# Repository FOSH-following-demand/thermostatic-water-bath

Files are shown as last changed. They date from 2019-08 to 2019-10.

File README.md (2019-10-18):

# Open Source Thermostatic Water Bath 



### Welcome!


Thanks you for visiting this repository of this wonderful project!.

This document (The README file) is a hub to give you some guidance about all of what is happening here.

If you want to know more, please follow this quick links to jump to a specific section, or just scroll down to find out more!
  * [The problem involved](https://github.com/FOSH-following-demand/thermostatic-water-bath#the-problem)
  * [The solution we found](https://github.com/FOSH-following-demand/thermostatic-water-bath#the-solution)
  * [The idea behind the project](https://github.com/FOSH-following-demand/thermostatic-water-bath#the-idea)
  * [What we found interesting? ](https://github.com/FOSH-following-demand/thermostatic-water-bath#what-we-found)
  * [Find out more about](https://github.com/FOSH-following-demand/thermostatic-water-bath#get-involved)
  * [I don't understand something](https://github.com/FOSH-following-demand/thermostatic-water-bath#glossary)

## The problem:

In research and clinical laboratories, it is always useful to keep reagents or samples that are analyzed, at certain temperatures.
A _thermostatic bath_ is a device designed to maintain the temperature of the objects in contact with the fluid used.

In general, they are composed of electric heaters that heat distilled water (or other fluid) and, when they reach a certain temperature, they are automatically disconnected from the energy.

## The solution:

Our idea is to use efficiency and solidity as a basis, so we will use Peltier cells to take advantage of the Peltier effect, which is normally used as a thermoelectric cooler.

But, the advantage of using these cells, is that if we reverse the polarity, we could extract heat instead of generating it.

Therefore, we would have a thermostatic bath capable of generating heat or cold without modifying its design or changing any part.

The project will consist on the design and construction of the control circuit as well as the hardware involved, e. g. bath container, dissipation of heat, etc.

### The idea

The microcontrollers based on the [ATMEGA328p](https://store.arduino.cc/usa/arduino-uno-rev3) will be used mainly for the first tests and the calibration of the sensors.
```
Once this is done (by the way, you can check the code [here](https://github.com/FOSH-following-demand/thermostatic-wather-bath/tree/master/software/MCU)), the goal will be to use a __"We Mos D1 Mini"__ [board](https://wiki.wemos.cc/products:d1:d1_mini) as the main controller and, as a complement, the ability to connect to [Cayenne web services](https://mydevices.com/) as a monitor and remote control through IoT technology.
```
While this was a good idea, in the end, we are going to use a "_NODEMCU-32S_", The [NodeMCU ESP-32S](https://docs.zerynth.com/latest/official/board.zerynth.nodemcu_esp32/docs/index.html) is one of the development board created by NodeMcu to evaluate the ESP-WROOM-32 module. It is based on the ESP32 microcontroller that boasts Wifi, Bluetooth, Ethernet and Low Power support all in a single chip. Then, an internet connection will be built through the use of the [Mozilla WebThings Open Source IoT](https://iot.mozilla.org/) platform, which will be centralized in a hub ([Raspberry Pi 4](https://www.raspberrypi.org/products/raspberry-pi-4-model-b/)) for later operation and remote control.

The electric resistors if they do not have water are burned (if they do not have electronic protection circuits, as usual), with the design proposed in this project, we will try to avoid it by measuring the current that the cell consumes, so we can determine, without using another type of sensors, like a __DS18B20__ ([datasheet here](https://datasheets.maximintegrated.com/en/ds/DS18B20.pdf)), if the container where the piece is located, has enough distilled water or coolant (in case you want to cool below 0 deg C).

There is a lot of variety of Peltier cells, qualities and ways to get them. We have been guided by a Chinese manufacturer ([link here](https://peltiermodules.com/)) that briefly describes the characteristics of the product, but when we go to the tests, they perform as stated in the datasheet.

## What we found

In our studies, we used a Peltier Cell [TEC-12705](https://peltiermodules.com/peltier.datasheet/TEC1-12705.pdf) to start. After many thorough tests, we realized that it would not be able to heat quickly the water in the container (around 1 liter). Therefore, after a week of continuous tests, we change to a _new cell_, in this case, the [TEC-12715](https://peltiermodules.com/peltier.datasheet/TEC1-12715.pdf), which may seem only a little bigger than the 12705, but while the power of the 12705 is __50W__, the one of the 12715 is __150W__!

We had to get a more powerful 12v power supply, which are frequently used in DVR cameras, approximately 29 A of peak current, to improve the power.

We have managed to stabilize the temperature adequately in the range of +/- 0.1 °C, which made us very happy! Here are some [results](https://docs.google.com/spreadsheets/d/14x8ajXjDDJAvYHkvkYrGuCvhuu2BmfRY7JI32HTowtU/edit?usp=sharing).

[Here](https://docs.google.com/spreadsheets/d/1heXNcq8TzLmtxA4aUKqf4gO-YtcK64AZdO5G_QmcZ0U/edit?usp=sharing) is the most complete example on the peltier usage.

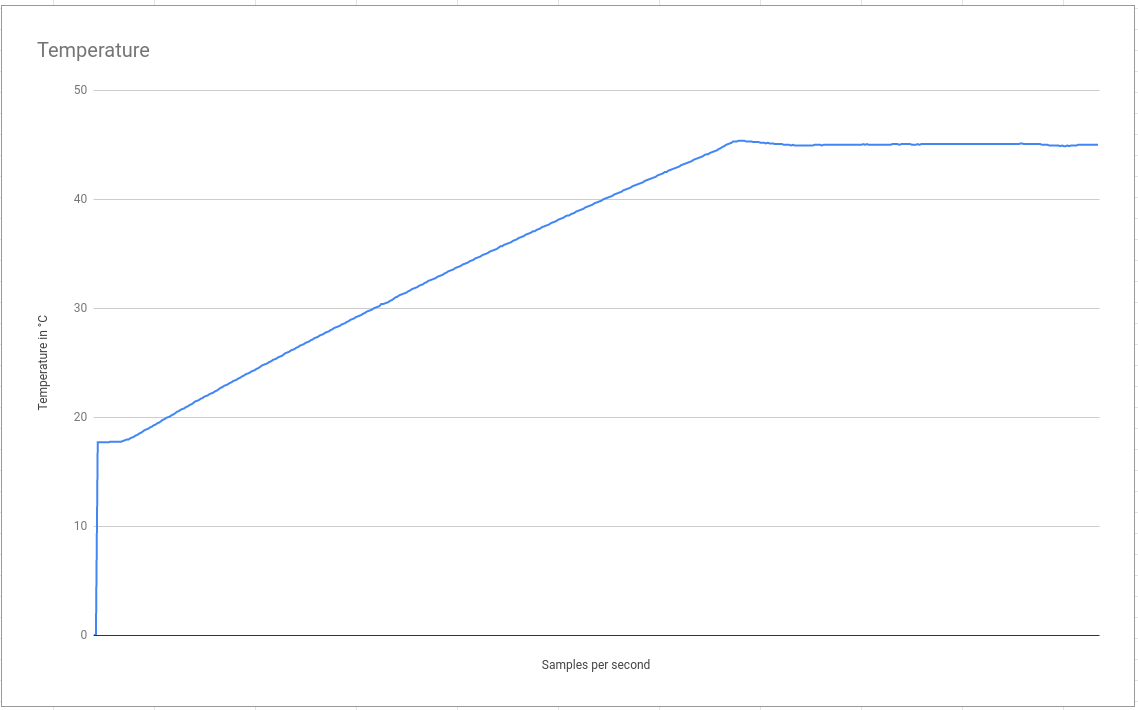
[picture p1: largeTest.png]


## Get involved

### Contribute
As we move forward, we will be contributing more and more things to the repository, if you like this project please contribute to it, after reading the [contributing](https://github.com/FOSH-following-demand/thermostatic-water-bath/blob/master/contributing.md) scheme.

### Development Plan

To follow the last changes made in the project, please follow this [link](https://github.com/FOSH-following-demand/thermostatic-water-bath/blob/master/dev_plan.md)

### Construction and Building

  To continue with the _Installation of Software_, please follow this [link](https://github.com/FOSH-following-demand/thermostatic-water-bath/tree/master/software/MCU)

  To continue with the _Building of Electronics_, please follow this [link](https://github.com/FOSH-following-demand/thermostatic-water-bath/tree/master/documentation/building)

  To continue with the _Building of the Hardware_, please follow this another [link](https://github.com/FOSH-following-demand/thermostatic-water-bath/blob/master/hardware/BOM/BOM.md)

  To continue with the _Building of the frame_, please click [here](https://github.com/FOSH-following-demand/thermostatic-water-bath/blob/master/hardware/frame/frame.md#3d-design-files-are-here)

### Thank you

by [TECSCI](https://github.com/tecsci)

### Glossary

  * __README File__: a document that introduces an open project to the public and any potential contributors
  * __repository__ or __repo__:a collection of documents related to your project, in which you create and save new code or content
  * __Issue__: the GitHub term for tasks, enhancements, and bugs for your projects

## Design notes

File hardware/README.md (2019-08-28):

# Hardware

This video made with a thermal camera shows us what the system is capable of.

Video

The settings that have been made for this video correspond to the software version 0.0.2

### Current features [version 0.0.2]:

If the sensor is not correctly connected at the beginning of the program, an alarm will be triggered that the only way to update it will be by restarting the microcontroller.

Video

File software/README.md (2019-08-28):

_Two libraries_ are currently being used, possibly 2 more would be missing, to improve the code.

One is called "__Peltier__" and the other is called "__lcdScreen__", both are designed to simplify the Arduino code and not make it so tedious to read and understand in order to modify it.

In effect, the libraries have given more work time since they needed a lot of testing and debugging,

With the PID control, most of the incidents have occurred, since although our setup was within the parameters taught in the code, their behavior was not very desirable and what was called an overshooting above the setpoint occurred, This led to a hunting and debouncing very frequently seen in these types of cells.

In addition to the challenge of using peltier cells for the thermostatic bath, we can say that the interest aroused by the use of them has generated more than one query in our group of nearby people.

Now we continue with the description of the libraries

# Available Commands on
- Peltier Library

```
createPeltier(uint8_t A,uint8_t B,uint8_t E, uint8_t pwm);

void coolFast();

void heatFast();

bool cool(bool activate, uint8_t pwmValue);

bool heat(bool activate, uint8_t pwmValue);

bool powerOff(bool confirm);

```
You have two options, one is to use a Driver as we will suggest later, although the other most frequently used is to use a Relay connected to one of the pins (In this case it would be the "Enable" pin you have defined), while that with the other system using a driver, you will not only be able to cool and heat without moving any electrical connection, but you will also have the possibility of using a PID control in your setup for temperature control.

- LCD Screen Library  (It is currently under development :fire: ...)
```
  initThis(char addr, int rows);

  bool turnOff();

  bool setActualTemp(float num);

  bool setCurrent(float amps);

  bool setEndTemp(float set);
```
This library facilitates the assembly of the user interface on the LCD screen (small GUI), it can be 16x02 or 20x4, both can be set in the library and thus automatically accommodate the parameters on the screen.

The connections and lcdScreen library will be put shortly, after solving some short-circuit problems in the code :suspect:

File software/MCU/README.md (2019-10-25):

# Version history







### Program 0.0.1 (Alpha)
  First version of the software
  * it uses the most crude code as possible
  * all the sensors and current measuring
  * the kp, ki and kd was not set in the code.
  * Baud-rate set to 9600

### Program 0.0.2 (Squeeze)
  First stable program
  * Added new custom characters to the lcd screen.
  * the Current sensor was eliminated
  * the kp and kd where set in function with the experiment
  * Baud-rate set to 19200
  * It uses P-D control to stabilze the temperature, while trying to get the set temp as fast as possible, it includes all the functions in the main sketch.

### Program 0.0.3 (Buster)
  First program to include the custom libraries to test it by __ONLY HEATING__
  * peltier library was _included_ in the folder, and updated in the __library__ folder
  * First program to use object-orientated peltier functions.

### Program 0.0.4 (Woddy)
  Last program to use the Arduino UNO Architecture, (microcontroller ATMEGA328-P)
  * This is the first program that can use the basic PID control, not only PD
  * kp, ki, and kd were set in two different ways, one in _aggresive mode_ and the other in _conservative mode_ ([What is this?](https://github.com/FOSH-following-demand/thermostatic-water-bath/blob/master/documentation/using/PID_Tunning%20Guide_Rice.pdf))
  * new routines for interrupts, they are used to change the setpoint, every turn makes +.1 °C in clockwise rotation and -.1°C in counterclockwise. [how to connect?](link)
  * The peltier library is located [here](https://github.com/br3ttb/Arduino-PID-Library/), [how to use it?](https://playground.arduino.cc/Code/PIDLibrary/)

  You'll need to install __Adafruit_BME280__ and __Adafruit_Sensor__ in order to try this sketch, refer to [0.0.5](https://github.com/FOSH-following-demand/thermostatic-water-bath/tree/master/software/MCU#program-005) to learn how to.

### Program 0.0.5 (Buzz)
  __NEW Architecture__: Now we're using the _NODEMCU-32S_ for the project, the peltier library was converted (But is in testing) to use
  analogWrite function (because ESP32 doesn't have the function to do that)
  * It uses the PID Control used in [0.0.4](https://github.com/FOSH-following-demand/thermostatic-water-bath/tree/master/software/MCU#program-004), with the kp,ki and kd tunned for the main construction.
  * There was added a BMP280 sensor to check the ambient temperature, so we can calculate the maximum and minimum temperature of the equipment, [How to connect ?](link)
  * The interrupts routines were eliminated, because in the new architecture this is not mandatory.
  * The peltier library is located [here](https://github.com/br3ttb/Arduino-PID-Library/), [how to use it?](https://playground.arduino.cc/Code/PIDLibrary/)

  You'll need to install __Adafruit_BME280__ and __Adafruit_Sensor__ in order to try this sketch.
  * [How to install Adafruit_Sensor in Arduino IDE?](https://www.arduinolibraries.info/libraries/adafruit-unified-sensor)
  * [How to install Adafruit_BME280 in Arduino IDE?](https://learn.adafruit.com/adafruit-bme280-humidity-barometric-pressure-temperature-sensor-breakout/arduino-test#install-adafruit-bme280-library-4-7)

### Program 0.0.5 (Lenny)

  * __Using the _NODEMCU-32s__: First version to include Tasks and multi-core processing of them.
  * It uses the PID Control used in [0.0.5](https://github.com/FOSH-following-demand/thermostatic-water-bath/tree/master/software/MCU#program-005), with the kp,ki and kd tunned for the main construction.
  * The Peltier library was a bit modified to work with the new architecture
  * This program __IS NOT STABLE__ because has a lot of _crude code_, the tests aren't done yet for this program.
  * WIP : The interrupt routines and the connection between the tasks using global variables.
  * the BMP280 was eliminated, the funcion was very expendable.

### Program 0.0.6 (Sarge)
* __Using the _NODEMCU-32s__: Second version: Tasks and multi-core processing.
* _Queue_ testing, FREERTOS in Arduino IDE__
* This program __Might not work__
* Updated the tasks for managing the data.

### Program 0.0.7 (Mike)
* __Using the _NODEMCU-32s__: Third version: Tasks and multi-core processing.
* Baud-rate set to 115200
* Hard-coded HTML code to show data in the browser. (Requieres internet connection for showing some symbols)
* Added landed (crude) web page to set the _setpoint_
* Problem solved with the Global variables and the share between tasks: Only one archive _(.ino)__ for all and _no queues_

### Program 0.0.8 (Tango)
* __Using the _NODEMCU-32s__: Last version in the Arduino IDE.
* Final assambly without the [Mozilla IoT WebThings Framework](https://iot.mozilla.org/)
* Baud-rate set to 115200
* This code is marked as STABLE but with no release.

### Program 0.0.9 (Slinky)
* __Using the _NODEMCU-32s and PlatformIO Framework__ --> [how to install PlatformIO?](https://platformio.org/install/ide?install=atom)
* _We need ATOM enviorment_ --> [how to install the last version of Atom?](https://atom.io/)
* In the source code located in /src/main.cpp you have to mannualy __set the SSID and the password of your WiFi Network__
* This program __only reads the temperature of the ds18b20 sensor and then send it to the WebThings Server__  --> [How to build one on a Raspberry Pi 3?](https://iot.mozilla.org/docs/gateway-getting-started-guide.html)
* Project name _webthing demo_, no screen, no PID Control, no setpoint.
* Baud-rate set to 115200
* __Very important!__: specific version of libraries are required to compile and run in the , _webthing-arduino 0.0.9_ , _PageBuilder 1.3.4_ and _arduinoJson 5.13.4_. the last one took a lot to catch...

# How to work with this programs? (from Version 0.0.1 to 0.0.7)

To test this sketch's, you must install the library included in the arduino database.

in order to do this, let's go to Library Manager of the __Arduino IDE__, located in

_Program --> Include library --> Library Manager_

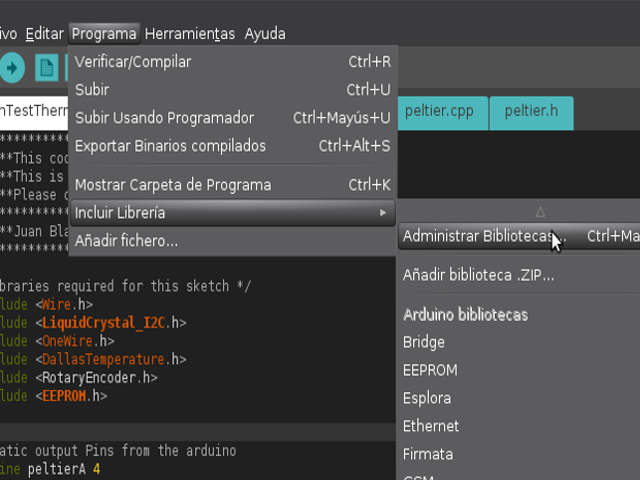
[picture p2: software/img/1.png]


then, you can install the lastest version of the _dallasTemperature_ after searching for it
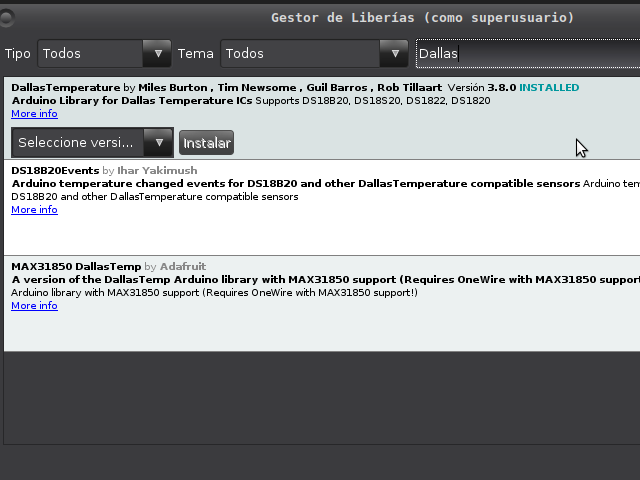
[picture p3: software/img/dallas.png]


In order to setup the LCD, you __must__ install the _LiquidCrystal_I2C_ library, __NOT__ the LiquidCrystal
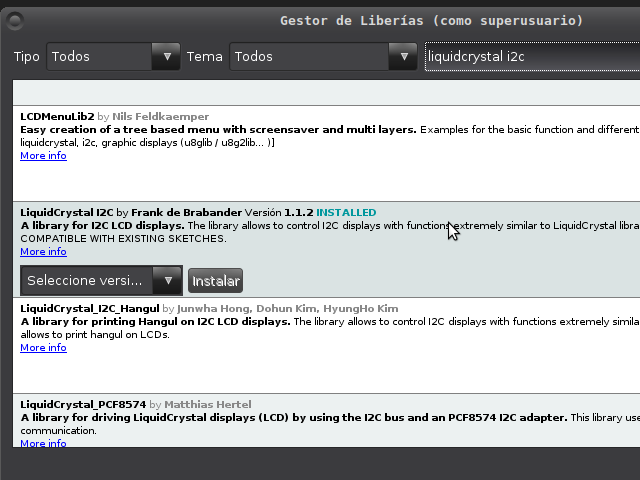
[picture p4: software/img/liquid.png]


The last remaining item, is the __oneWire__ library to control the _DS18B20_ sensor.
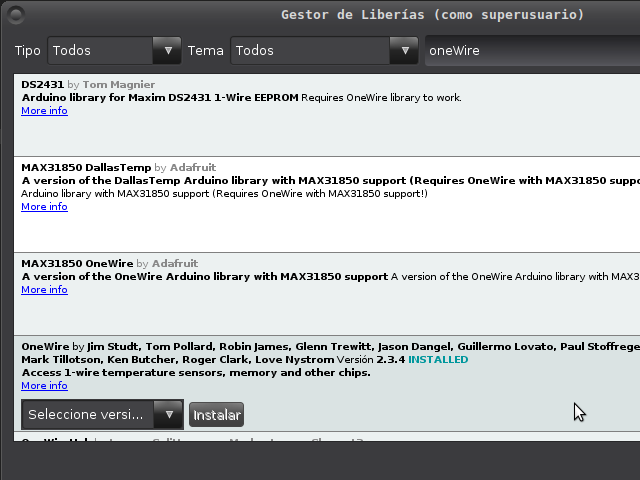
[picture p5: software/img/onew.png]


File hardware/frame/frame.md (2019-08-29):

# 3D Design Files are here

By now, the only version of the bath is V2, because V1 was __lost__ in a broken usb stick :(

## Files included:

  * ThermostaticWaterBathv1.stl : __Missing File :(__

  *  ThermostaticWaterBathv2.stl : Second version of the housing, _includes the bottom_ of the box separately, with rubber feet designed

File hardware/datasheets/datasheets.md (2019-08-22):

#### Datasheet for the Thermostatic water bath

Here we left the datasheets of the components than we used

* VNH3SP30 Motor Driver

* TEC1-12715 Peltier Cell

* Power Supply 12v 29A Pronext 

* Arduino UNO

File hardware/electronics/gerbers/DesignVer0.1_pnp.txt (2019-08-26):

*Pick And Place List
*Company=
*Author=
*eMail=
*
*Project=DesignVer0.1
*Date=16:15:10
*CreatedBy=Fritzing 0.9.3b.04.19.5c895d327c44a3114e5fcc9d8260daf0cbb52806
*
*
*Coordinates in mm, always center of component
*Origin 0/0=Lower left corner of PCB
*Rotation in degree (0-360, math. pos.)
*
*No;Value;Package;X;Y;Rotation;Side;Name
1;5V;;68.4058;-10.8142;0;Bottom;Componente3
2;;;71.7105;-69.4247;0;Bottom;Power plug1
3;;;51.5111;-14.5291;0;Bottom;Via8
4;;;35.0519;-9.65234;0;Bottom;Via7
5;22µF;100 mil [THT, multilayer];29.2608;-23.519;90;Bottom;C1
6;;;6.4008;-71.7742;0;Bottom;Peltier element
7;;;27.7367;-15.1387;0;Bottom;Via3
8;;;72.8471;-34.0363;0;Bottom;Via1
9;;;31.3208;-53.6682;-90;Bottom;MD03A1
10;;THT;26.8064;-17.1635;0;Bottom;XTAL1
11;;THT;63.5508;-22.2442;90;Bottom;lcdScreen
12;;;49.6823;-15.7483;0;Bottom;Via6
13;22µF;100 mil [THT, multilayer];24.1808;-23.519;90;Bottom;C2
14;;;71.6279;-39.5227;0;Bottom;Via4
15;;;53.3399;-19.4059;0;Bottom;Via5
16;4.7k;THT;77.5208;-55.2642;180;Bottom;R1
17;;;6.57572;-7.00853;90;Bottom;DS1
18;5V;DPak [SMD];77.5209;-35.1841;0;Top;U2
19;;;16.7639;-28.5499;0;Bottom;Via2
20;1µF;100 mil [THT, electrolytic];66.0908;-32.4042;0;Bottom;C4
21;1µF;100 mil [THT, electrolytic];78.7908;-47.6442;0;Bottom;C3
22;;dip;33.0708;-8.27415;90;Bottom;U1

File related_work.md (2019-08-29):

# Related projects

These projects are linked to the research than was made for it, as showned in [Research and first tests](https://github.com/FOSH-following-demand/thermostatic-water-bath/blob/master/dev_plan.md#week-1-research-and-first-tests)

In the meantime, there are a lot of tools made, but none of them are Open Source at all, so this push forward the investigation about this construction.

## Here are the results currently found [29/08/19]

| Project name  | URL           | Active/Not active | Notes - relevance |
| ------------- | ------------- | ----------------- | -------------- |
| TLK33 | https://www.ascontecnologic.com/it/refrigerazione/regolatori-speciali/controllo-celle-di-peltier/tlk33 | Active |  Peltier cell regulator (Italian Company)  |
| Heating and Cooling with a Peltier Controller  |  https://www.meerstetter.ch/compendium/heating-and-cooling-with-a-peltier-controller  | Active |  TEC Controllers |
| Low Temperature Water Bath (Programmable, Peltier Cooling)BV100 |  https://www.yamato-scientific.com/product/show/bv100_2/  | Active  |  Space saving low temperature water bath with program operation function, high precision temp. control and low vibration type with Peltiert device equipped  |
|  Kruss PT31  | https://www.coleparmer.in/i/kruss-pt31-peltier-thermostat-recirculating-bath-8-to-40c-115-230v/1293012  |  Active  | Controls the temperature of refractometers, polarimeters, and other equipment  |
|  Peltier-Type Chiller Thermo-con/Rack Mount Type  |  https://www.smcworld.com/products/pickup/en-jp/temperature_controller/incubator_pro.html  | Active  |  Can precisely control the temperature of a heat source or process fluid  |

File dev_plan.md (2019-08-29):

# Development plan

| Week        | Activities               | Who           |
| ----------- | ------------------------ | ------------- |
| 1           | Research and firsts tests|  @juanstdio   |
| 2           | first version 0.0.1      |  @juanstdio   |
| 3           | create libraries         |  @juanstdio   |
| 4           | make schematics & BOM    |  @juanstdio   |
| 5           | update BOM & PCB 0.0.2   |  @juanstdio   |
| 6           |                          |               |
| 7           |                          |               |
| 8           |                          |               |

### Week 1: Research and first tests

We research about the peltier elements, the basis of how they work, and we found papers about this in the __IEEE xplore__ titled _"A low-cost temperature controlled system to test and characterize sensors"_
[LINK](https://ieeexplore.ieee.org/abstract/document/1406715).
```
Abstract:
Almost all parameters (physical and chemical) used for in-situ water quality monitoring of rivers and seas, are measured using sensors that have characteristics highly sensitive to temperature.
The objective of this paper is to present the project, design and implementation of a low cost testing bath with automated temperature control for environmental monitoring sensors characterization.
Besides the description of the overall testing system, the paper details the cooling and heating thermoelectric pump based on Peltier modules implemented for the temperature control of the liquid, the tests that were conducted in order to obtain its optimal performance, the set of sensors and their signal conditioning to measure the temperature and the digital proportional-integral-derivative (PID) algorithm implemented in LabVIEW to control the temperature of the bath.
The developed testing apparatus proved to be an efficient tool to test and characterize sensors for in-situ water quality monitoring
```

Also at [Researchgate](www.researchgate.net/) we found another example of the using of the peltier elements,_"Peltier based cabinet cooling system using heat pipe and liquid based heat sink"_ [LINK](https://www.researchgate.net/publication/271459963_Peltier_based_cabinet_cooling_system_using_heat_pipe_and_liquid_based_heat_sink)
```
Abstract:
This paper describes a peltier based cabinet cooling system using heat pipe and liquid based heat sink.
Two peltier devices are used for increasing cooling effect.
Heat transfer effectiveness through peltier device is increased by using heat pipe based heat sink attached with fan and liquid based heat sink.
The hot side of both the peltier device is attached to same liquid based heat sink and cold side is attached to heat pipe based heat sink.
The coolant (water) inside the liquid based heat sink absorbs the heat from the hot side of both the peltier devices and then circulated through radiator.
The fins inside the radiator absorb heat from the liquid and give it back at lower temperature to the container.
Again the cold liquid from container pumped into the liquid based heat sink and same cycle repeats.
The heat pipe based heat sink dissipates cold air inside the cabinet through fins.
Heat pipe and liquid based cooling is the most efficient method of heat removal, they are often 4 -5 times more efficient compared to a normal aluminium heat sink.
A controller circuit is designed and implemented for controlling the set temperature inside the cabinet.
Based on the temperature data sensed by the LM-35 sensor, the controller controls the power supply to the peltier device.
Experiments are conducted at different set temperatures and performance of peltier based cabinet cooling system is tested.
```

### Week 2: First version 0.0.1
link [here](https://github.com/FOSH-following-demand/thermostatic-water-bath/tree/master/software/MCU)

With all purchased components (drivers, peltier elements, cables, power supply, sensors and protoboards)
the first implementation of the code began, following a trial and error path, a code version was reached which "worked" but was not very neat for a final version, therefore it was quickly replaced by a new version, although we learned a lot with that first version.

Also, in the research of the papers, there was some new paper about peltier elements in Driving high brightness LED applied in specral measurements, also find in the [IEEE xplore ](https://ieeexplore.ieee.org/document/7428639)
```
Abstract:
A double closed-loop control system for driving high brightness LED to keep the temperature and emission intensity of LED stable is presented.
In one closed-loop control, a Peltier is used to control LED's temperature and its average power can be dynamically regulated as LED temperature changes.
In another, sampling real emission intensity of LED and comparing with expected intensity is repeatedly operated to make the real intensity follow the expected intensity.
Design of LED driving system is demonstrated, and the thermostatic control effect and stability of LED spectrum are tested.
The test results show that the error of LED temperature control is about 0.1°C corresponding to a center wavelength shift of 0.015 nm for a red LED and the emission intensity error for the same LED is within 0.1%.
```

### Week 3: Create libraries

The peltier library and lcdScreen library was created, written and debugged.
in the final conclusion, the lcd Screen does not work correctly, so today is not implemented.
example of using the peltier library are [found here](https://github.com/FOSH-following-demand/thermostatic-water-bath/tree/master/software/MCU/0.0.3)

### Week 4: Make schematics & BOM

Schematics were made to understand it, they are made in [Fritzing](https://fritzing.org/home/), a software to design in a simple way, and export the gerber files to do the BOM using the kitspace addon.

After that, it was uploaded to the repository [here](https://github.com/FOSH-following-demand/thermostatic-water-bath/tree/master/hardware).

### Week 5: update BOM & PCB 0.0.2

the new PCB have been corrected, because in the last revision there was a missing resistor in the DS18B20 sensor used for amplify the signal of DQ pin.
New [Schematic](https://github.com/FOSH-following-demand/thermostatic-water-bath/blob/master/hardware/electronics/DesignVer0.1_esquemático.png)

After that, the PCB was corrected in order to make the new resistor in an SMD package fit in there. Also, new headers of FTDI programmer kit were added

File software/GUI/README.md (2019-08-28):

### At the moment, the only GUI is the LCD Screen than is written in examples

:fire: :fire: Code must be tested with the screen or using the serial monitor of the device. :fire: :fire:

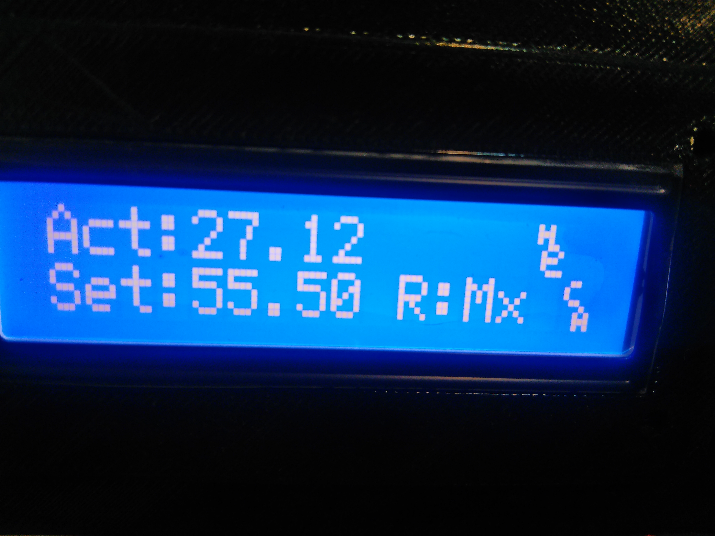
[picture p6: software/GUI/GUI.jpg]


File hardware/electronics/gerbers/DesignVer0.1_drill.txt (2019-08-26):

; NON-PLATED HOLES START AT T1
; THROUGH (PLATED) HOLES START AT T100
M48
INCH
T100C0.068569
T101C0.035000
T102C0.040000
T103C0.100000
T104C0.038000
T105C0.015748
T106C0.031496
T107C0.030556
T108C0.031555
T109C0.068555
T110C0.030000
%
T100
X011589Y029038
X009529Y029038
T101
X007520Y004757
X014520Y004757
X009520Y004757
X031520Y018757
X008520Y004757
X018520Y001757
X016520Y004757
X015520Y004757
X011520Y001757
X016520Y001757
X017520Y001757
X006520Y004757
X009520Y001757
X012520Y004757
X013520Y004757
X006520Y001757
X018520Y004757
X030520Y018757
X019520Y001757
X012520Y001757
X026520Y012757
X010520Y004757
X019520Y004757
X007520Y001757
X013520Y001757
X010520Y001757
X008520Y001757
X011520Y004757
X015520Y001757
X025520Y012757
X028520Y021757
X032520Y021757
X017520Y004757
X014520Y001757
T102
X022520Y004757
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

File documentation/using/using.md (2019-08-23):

## How to use the system

  1. __Getting started__

  When you upload the code to the Arduino, showned in the [building process](https://github.com/FOSH-following-demand/thermostatic-water-bath/blob/master/documentation/building/README.md), follow this steps

  2. __if you only want to test, please follow this__ [link](https://github.com/FOSH-following-demand/thermostatic-water-bath/tree/master/hardware/testing)

  3. __calibration steps__ _in progress of writing it_

  4. maintenance/storage information. _WorkInProgress_

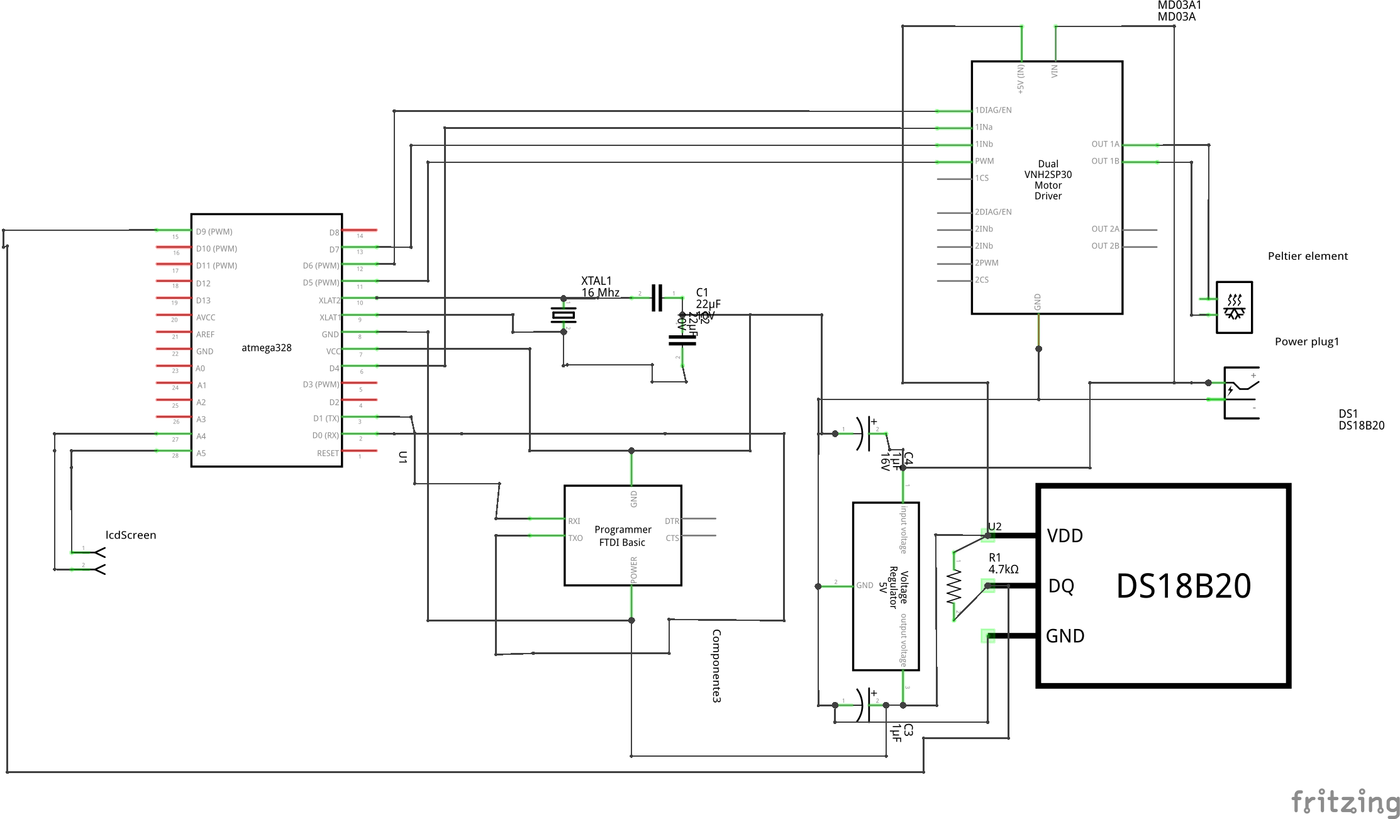
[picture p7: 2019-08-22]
hardware/electronics/DesignVer0.1_esquemático.png

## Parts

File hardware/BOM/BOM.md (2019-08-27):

#### Create BOM files for the equipment

- Mechanical_BOM.csv: Table containing all the mechanical parts necessary to build the equipment. Include here screws, printed parts, tubes, etc. See example below for fields

<br>

|part name| function  | quantity  |  obs.  |supplier|supplier number|link|
|---|---|---|---|---|---|---|
|M6x1 hex screws | used for holding motor in place  | 5  |  these could be substituted by flathead screws  |digikey| RPC6208-ND |https://www.digikey.co.uk/product-detail/en/essentra-components/SHSM6L16A/RPC6208-ND/9343049 |
|Peltier element  |  1  | 12v 150w peltier TEC1-12715 | DUAITEK |  TEC1-12715  | -  | - |  -  |  -  |  peltiermodules.com  |

<br>

- Tools_BOM.csv: table containing all tools used for the build. Pliers, hammer, etc.

<br>

|part name| function  | quantity  |  obs.  |supplier|supplier number|link|
|---|---|---|---|---|---|---|
|Nose needle Pliers  | hold components while soldering  | 1  |    regular pliers would also work   |digikey|L4VN-ND  |https://www.digikey.co.uk/product-detail/en/apex-tool-group/L4VN/L4VN-ND/8021129 |

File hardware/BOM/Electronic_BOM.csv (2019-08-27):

ID | Name | Designator | Footprint | Quantity | Manufacturer Part | Manufacturer | Supplier | Supplier Part
1 | DS18B20 | U1 | TO-92-3_3PIN-L4.70-W3.70-PITCH1.27-T | 1 | DS18B20 | Youtai Semiconductor Co., Ltd. | LCSC | C376006
2 | ATMEGA328P-PU | U2 | DIP-28_300MIL | 1 | ATMEGA328P-PU | MICROCHIP | LCSC | C33901
3 | FTDI_BASIC | JP1 | FTDI_BASIC | 1
4 | 16 Mhz Crystal | Q1 | HC49U-V | 1 |  |  | Mouser
5 | 22uF | U3,U4 | TWO_IO | 2
6 | POWER_JACK | J1 | POWER_JACK_PTH_BREAD | 1
7 | 7805 | U5 | TO220H | 1
8 | 1uF | C1,C2 | CAP-TAN-S2.5 | 2 | TAP105K050SCS | AVX | LCSC | C52309
9 | I2C_STANDARD | JP2 | 1X04 | 1
10 | POLOLU_VNH2SP30-MD01B-U | MOD1 | POLOLU_MD01B_U | 1
11 | Peltier_Element | PE2 | 40 BY 40 PELTIER | 1

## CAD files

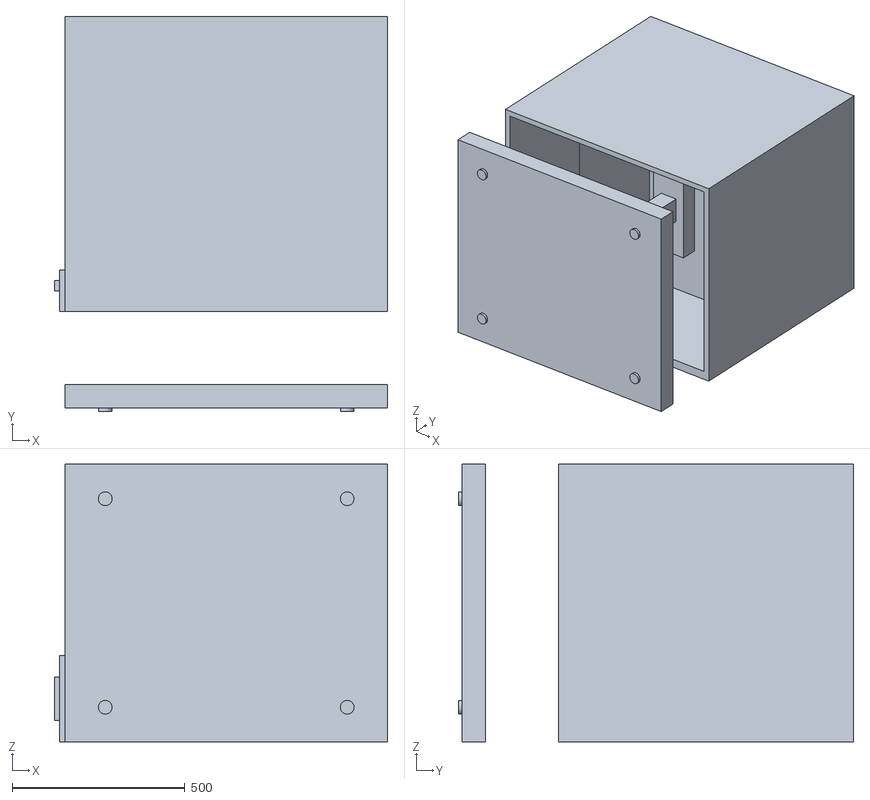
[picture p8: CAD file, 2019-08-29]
hardware/frame/ThermostaticWaterBathv2.stl
964.1 x 1144.2 x 804.9

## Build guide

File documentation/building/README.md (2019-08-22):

***Building instructions:***

<br>

### 1. __Getting started__

_How to upload the code to the arduino?_

  First, after downloading the arduino IDE for different [plataforms](https://www.arduino.cc/) and Configuring it as is showned [here](https://github.com/FOSH-following-demand/thermostatic-water-bath/tree/master/software/MCU) we need to upload the code.

  After cloning or downloading all the package, you'll download the last version of the code on the __/master/software/MCU__ directory (_actually is 0.0.2_).

  Now, you will open the arduino IDE, and an empty sketch will be loaded
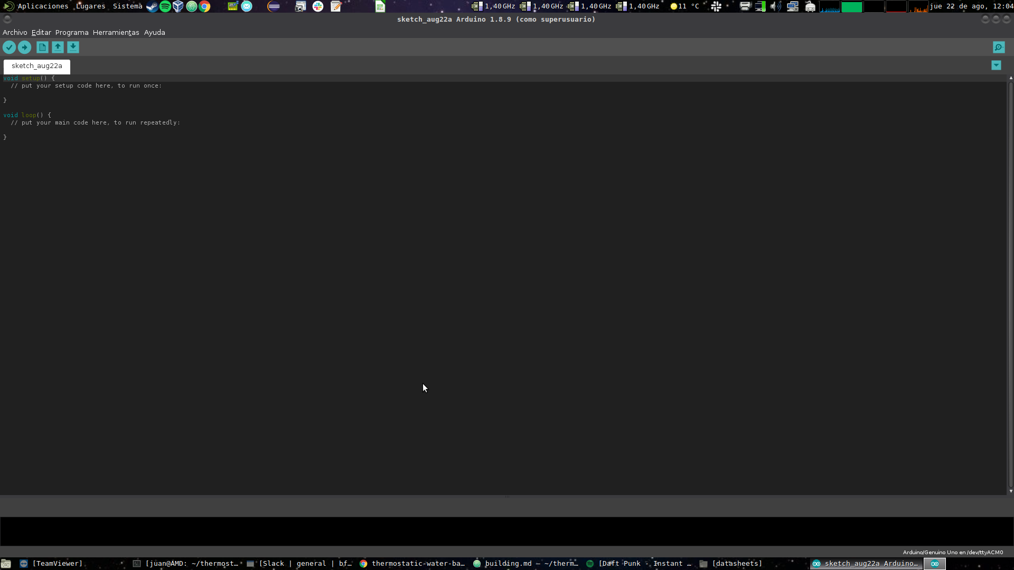
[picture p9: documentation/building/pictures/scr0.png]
  

  __To load a program__ you need to open the file called _0.0.2_ (the last version of the software)
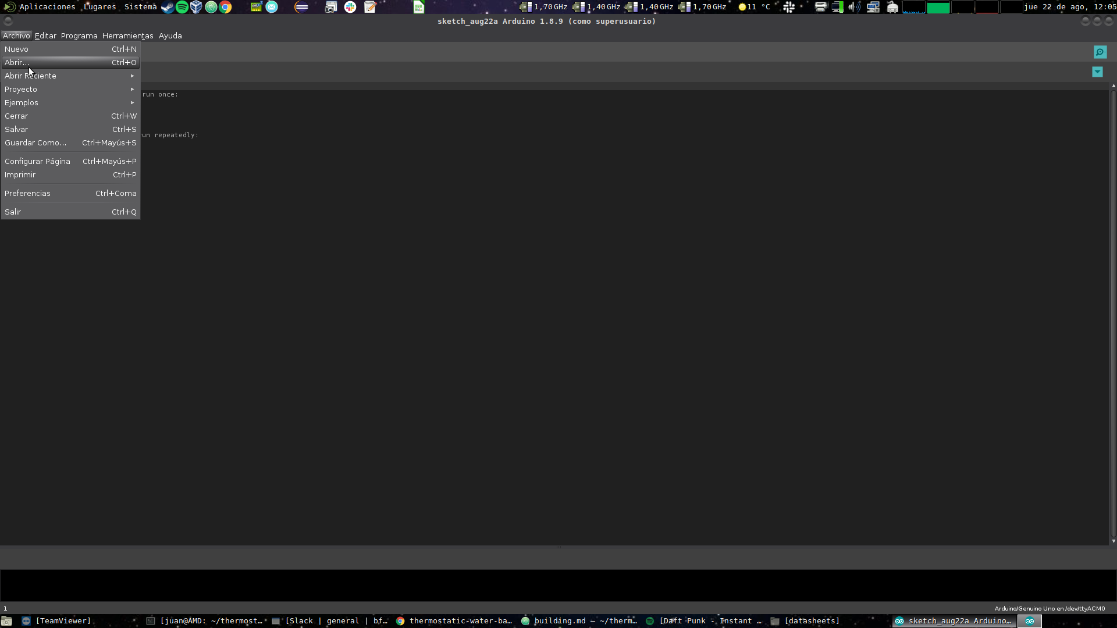
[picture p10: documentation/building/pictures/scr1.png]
  

  Click __Open__
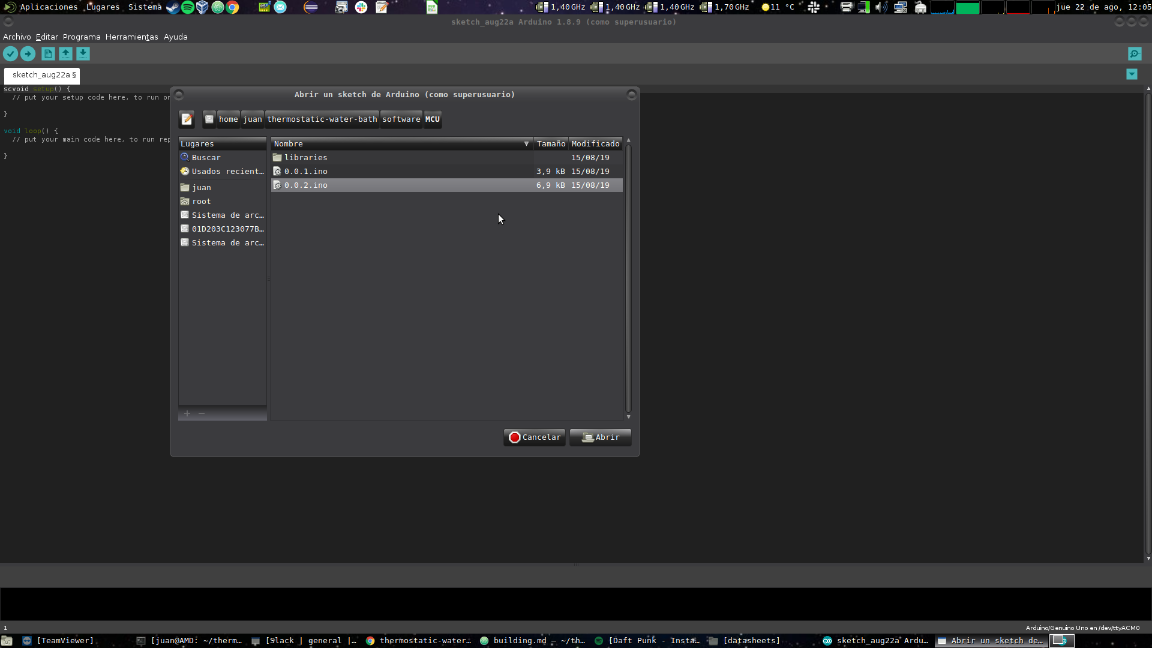
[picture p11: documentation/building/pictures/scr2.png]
  

  Once the program is loaded, you'll need to verify it using the Check button :heavy_check_mark: .

  if everything is correct, and the arduino is correcly connected based on the schematics, you can upload the code using the right arrow :arrow_right:

  __WARNING:__:warning:  Make sure than you selected the correct _microcontroller_ in the selection menu, as showned here
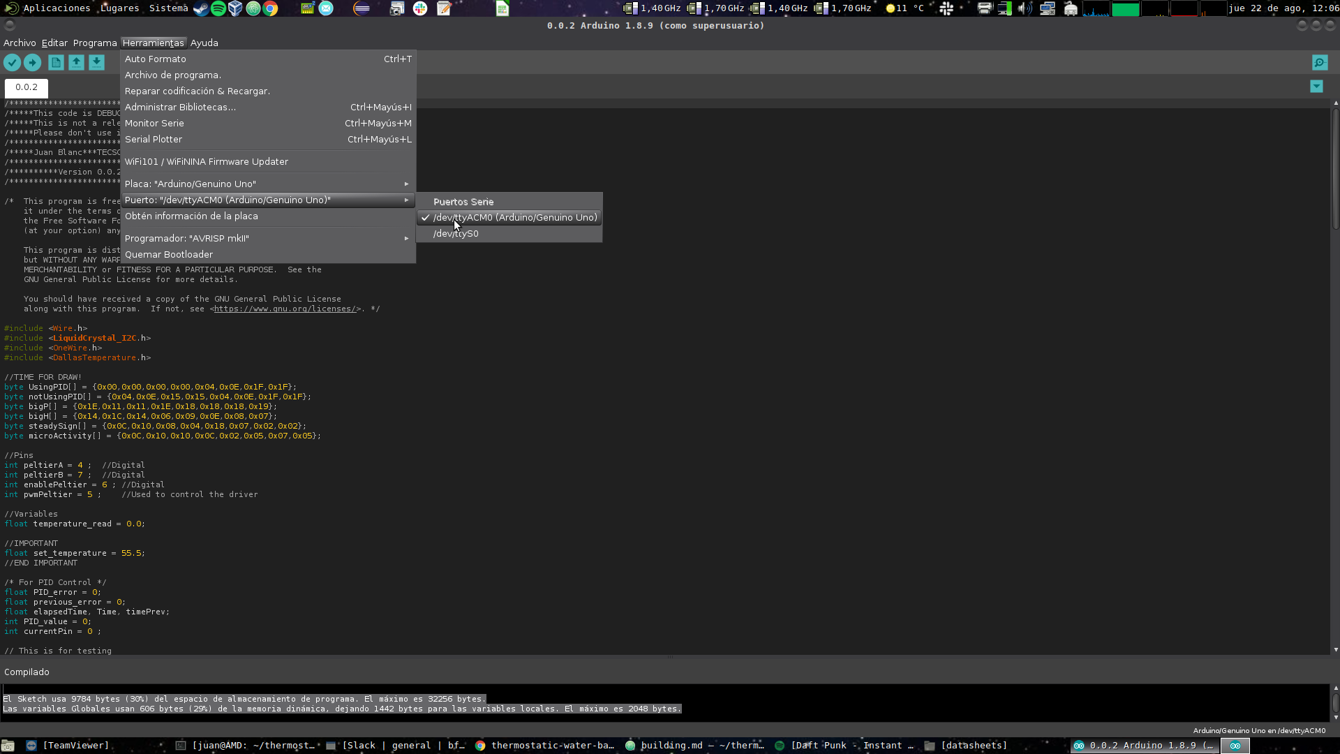
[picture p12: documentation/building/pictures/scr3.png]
  

  After that, you'll see the current temperature in the monitor of the Arduino Serial Monitor (you can use _crtl + shift + m_ as direct access) as showned on the end of the video.

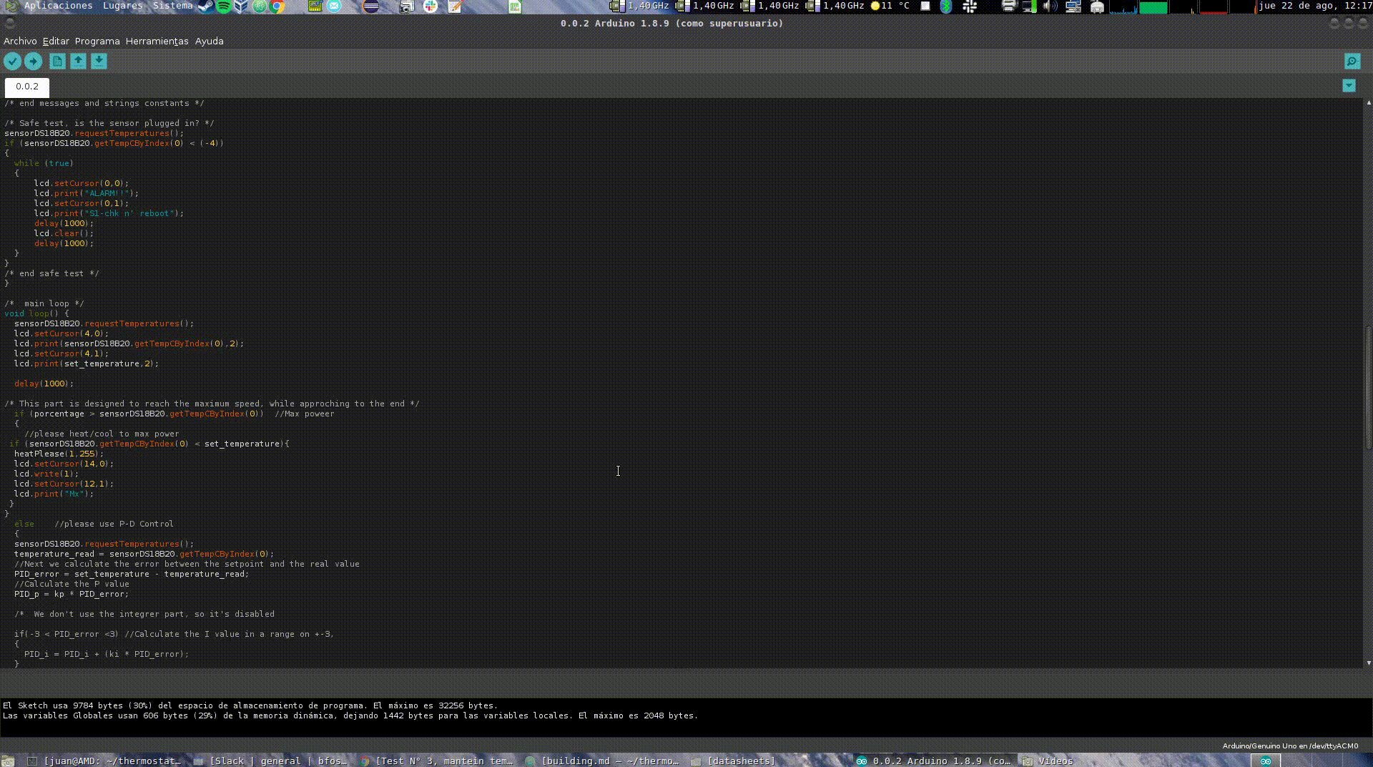
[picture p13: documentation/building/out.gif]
Video


### 2. List of materials needed:
  for the main electronics, We'll need the follwoing, as described [here](https://github.com/FOSH-following-demand/thermostatic-water-bath/blob/master/hardware/datasheets/datasheets.md) in the electronics datasheets files.

  * VNH3SP30 Motor Driver

  * TEC1-12715 Peltier Cell

  * Power Supply 12v 29A Pronext or equivalent.

  * Arduino UNO Rev 3

  * Heat Sink Grease

### 3. Build steps:
  * 3.a : Connect the OUT1A of the VNH3SP30 Driver to the _Black_ wire of the Peltier element.

  * 3.b : Connect the OUT1B of the VNH3SP30 Driver to the _Red_ wire of the Peltier element.

  * 3.c : Connect the EN of the VNH3SP30 Driver to the _Digital Pin 6_ wire of the Arduino UNO.

  * 3.d : Connect the INA of the VNH3SP30 Driver to the _Digital Pin 4_ wire of the Arduino UNO.

  * 3.e : Connect the INB of the VNH3SP30 Driver to the _Digital Pin 7_ wire of the Arduino UNO.

  * 3.f : Connect the PWM of the VNH3SP30 Driver to the _Digital Pin 5_ wire of the Arduino UNO.

  * 3.g : Connect the SDA of the lcdScreen to the _Analog input 4_ wire of the Arduino UNO.

  * 3.h : Connect the SCL of the lcdScreen to the _Analog input 5_ wire of the Arduino UNO.

  * 3.i : Connect the DQ of the DS18B20 to the _Digital Pin 9_ wire of the Arduino UNO.

  * 3.j : __Connect all the Ground pins of the lcdScreen and the DS18B20, and from the VNH3SP30__

  * 3.k : Connect all the 5v rails of the lcdScreen, the __DS18B20 with the 4,7K in parallel with DQ and VDD__ and the VNH3SP30, as shown in the schematic.

  * 3.l : Plug in the arduino uno and proceed to upload the sketch as showed below.

<br>

### 4. Last checks before powering up/using for the first time:
  :warning: :warning: __DO NOT POWER WITH 12v the peltier module without Heatsink !! it may burn your skii or cause damage to the driver.__ :warning: :warning:

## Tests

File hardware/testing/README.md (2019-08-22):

# Testing example

### This construction is used to test the peltier element and the driver at the same time, without using microcontrollers.

:hotsprings::hotsprings:__Please note that the peltier element must be crushed with heat sinks in both sides to prevent overheating__ :hotsprings::hotsprings:
### List of materials:

* VNH3SP30 Motor Driver

* TEC1-12715 Peltier Cell

* Power Supply 12v 29A Pronext or equivalent.

* Heat Sink Grease

### Build steps:
  * 1.a : Connect the OUT1A of the VNH3SP30 Driver to the _Black_ wire of the Peltier element. :heavy_check_mark:

  * 1.b : Connect the OUT1B of the VNH3SP30 Driver to the _Red_ wire of the Peltier element. :heavy_check_mark:

  * 1.c : Connect the EN of the VNH3SP30 Driver to 5v rails :heavy_check_mark:

  * 1.d : Connect the INA of the VNH3SP30 Driver to 5v rails :heavy_check_mark:

  * 1.e : Connect the INB of the VNH3SP30 Driver to GND rails :heavy_check_mark:

  * 1.f : Connect the PWM of the VNH3SP30 Driver to 5v rails :heavy_check_mark:

  * 2.a : power up the circuit with __12v__ from the plug, remember that the center is __Positive__ (VCC), and the outside is _negative_ (GND)

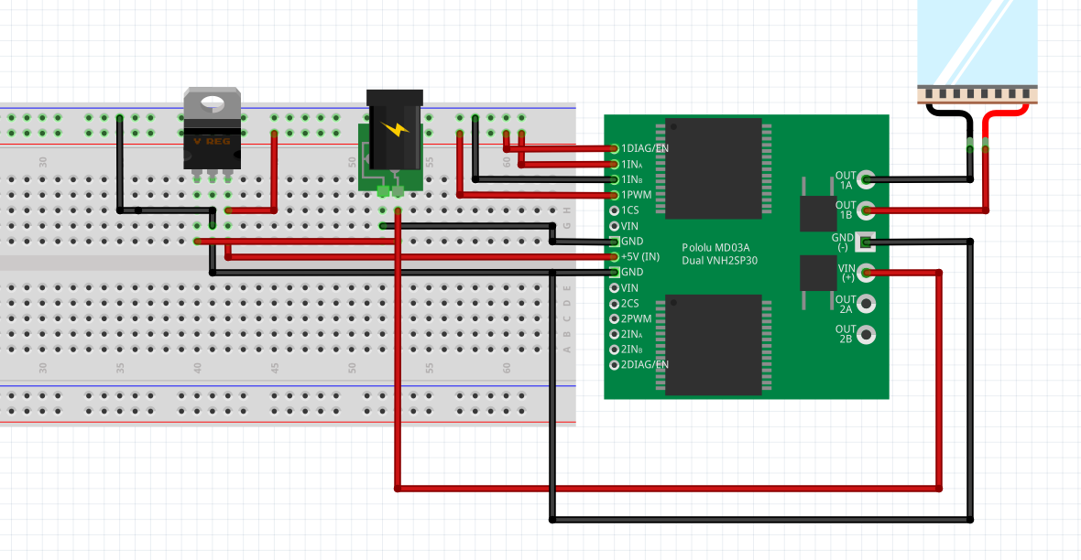
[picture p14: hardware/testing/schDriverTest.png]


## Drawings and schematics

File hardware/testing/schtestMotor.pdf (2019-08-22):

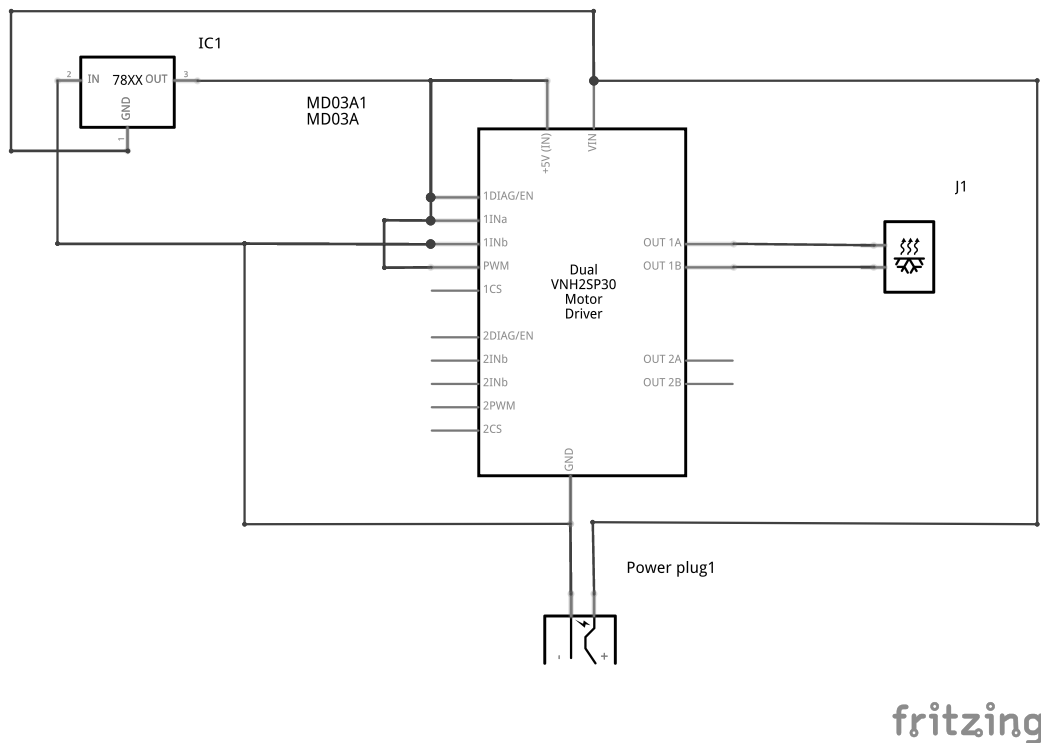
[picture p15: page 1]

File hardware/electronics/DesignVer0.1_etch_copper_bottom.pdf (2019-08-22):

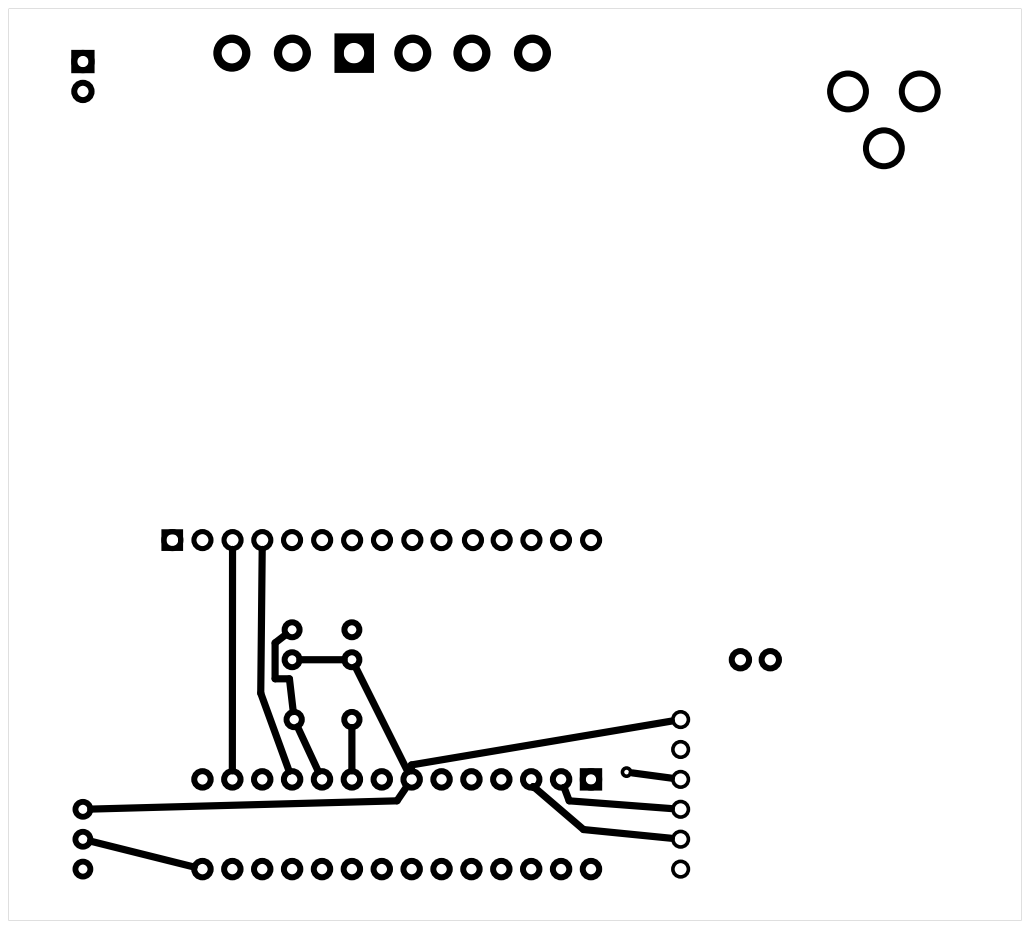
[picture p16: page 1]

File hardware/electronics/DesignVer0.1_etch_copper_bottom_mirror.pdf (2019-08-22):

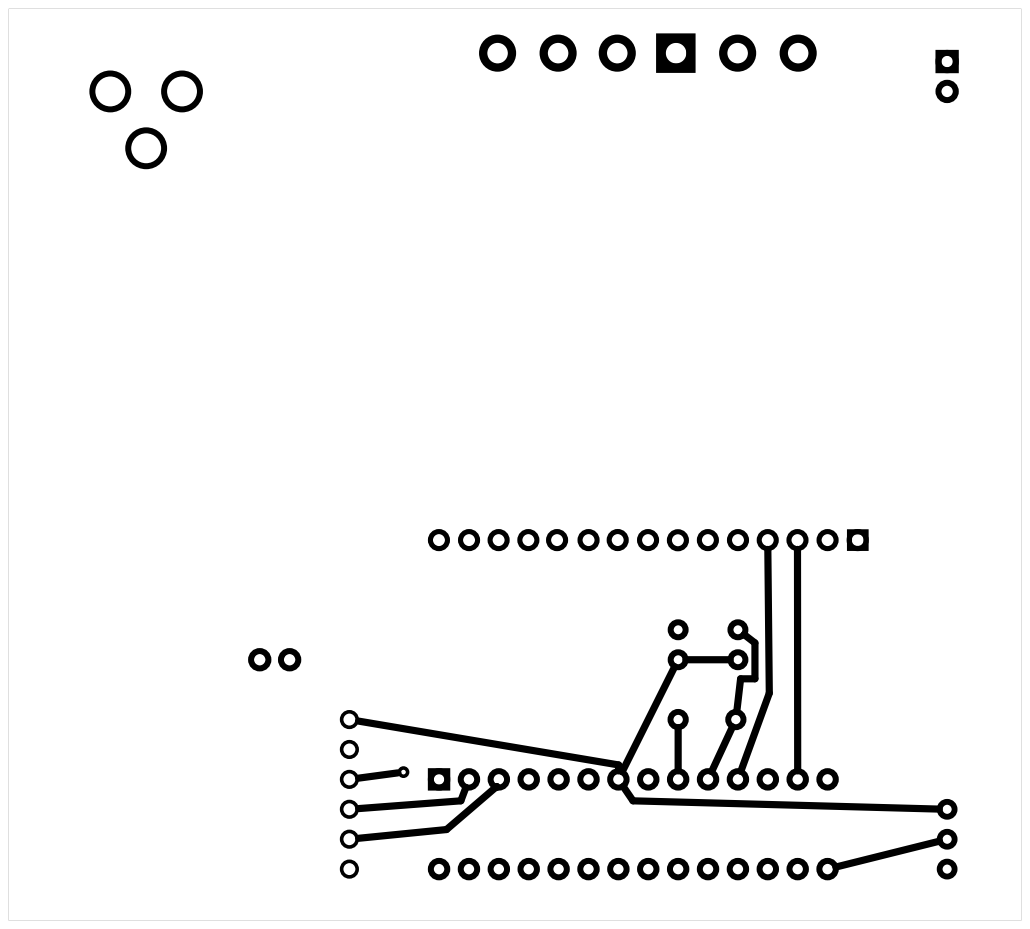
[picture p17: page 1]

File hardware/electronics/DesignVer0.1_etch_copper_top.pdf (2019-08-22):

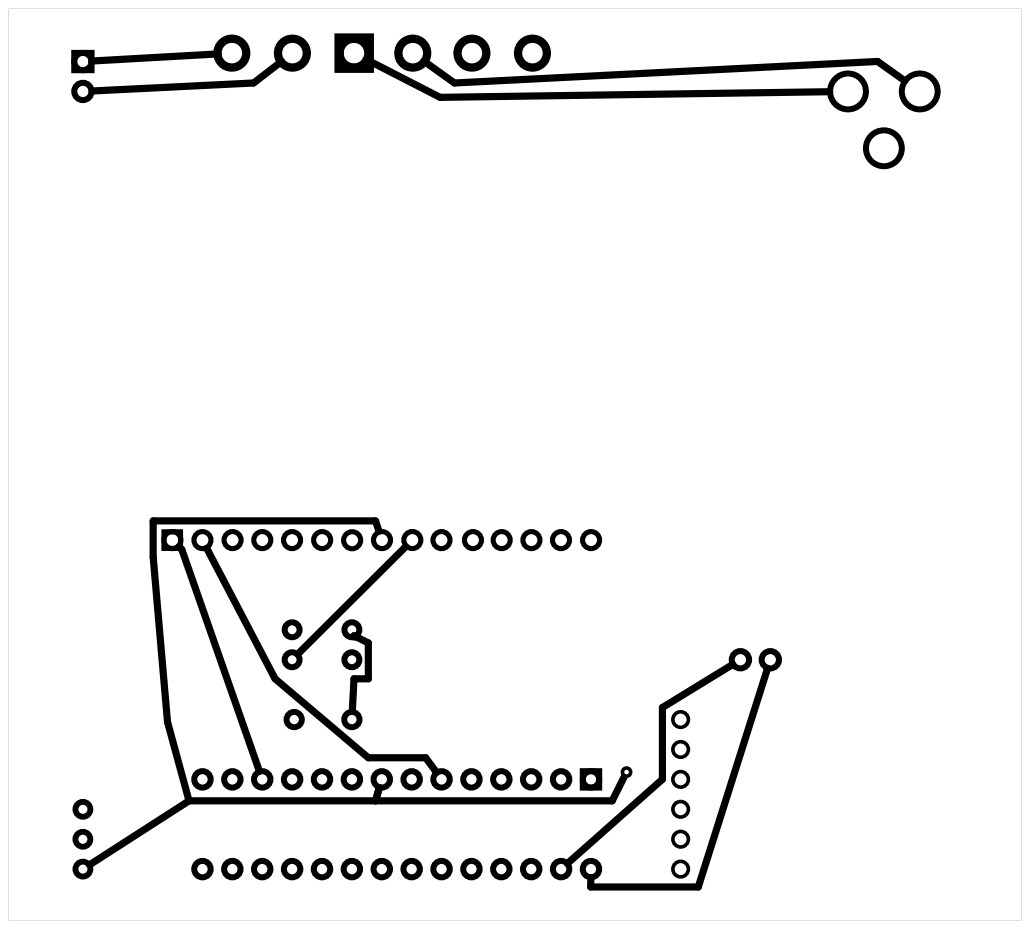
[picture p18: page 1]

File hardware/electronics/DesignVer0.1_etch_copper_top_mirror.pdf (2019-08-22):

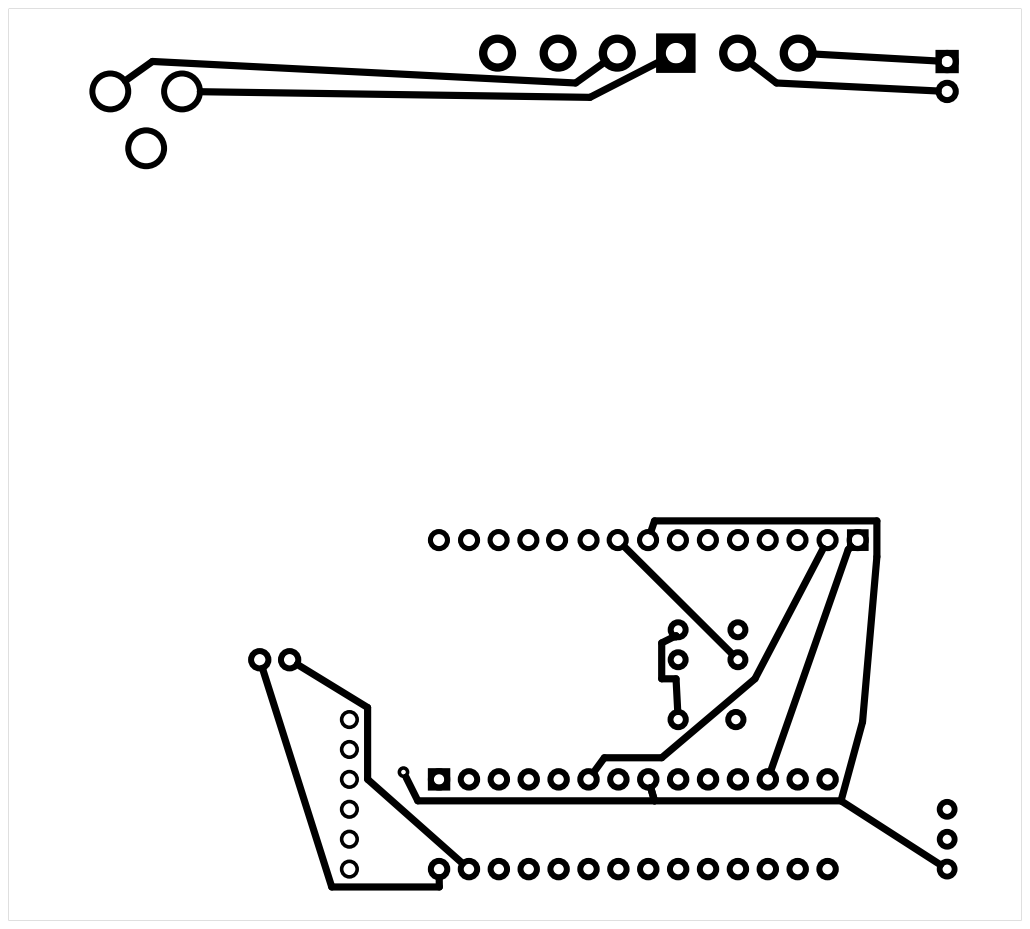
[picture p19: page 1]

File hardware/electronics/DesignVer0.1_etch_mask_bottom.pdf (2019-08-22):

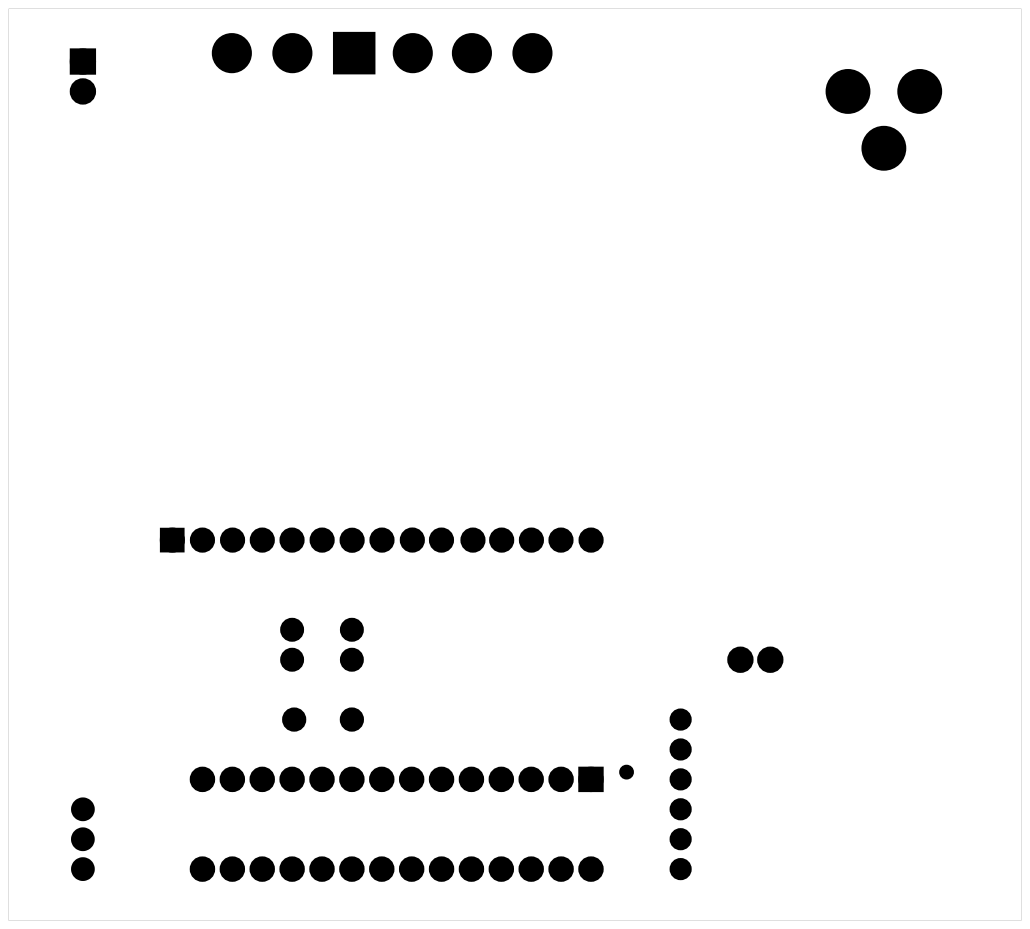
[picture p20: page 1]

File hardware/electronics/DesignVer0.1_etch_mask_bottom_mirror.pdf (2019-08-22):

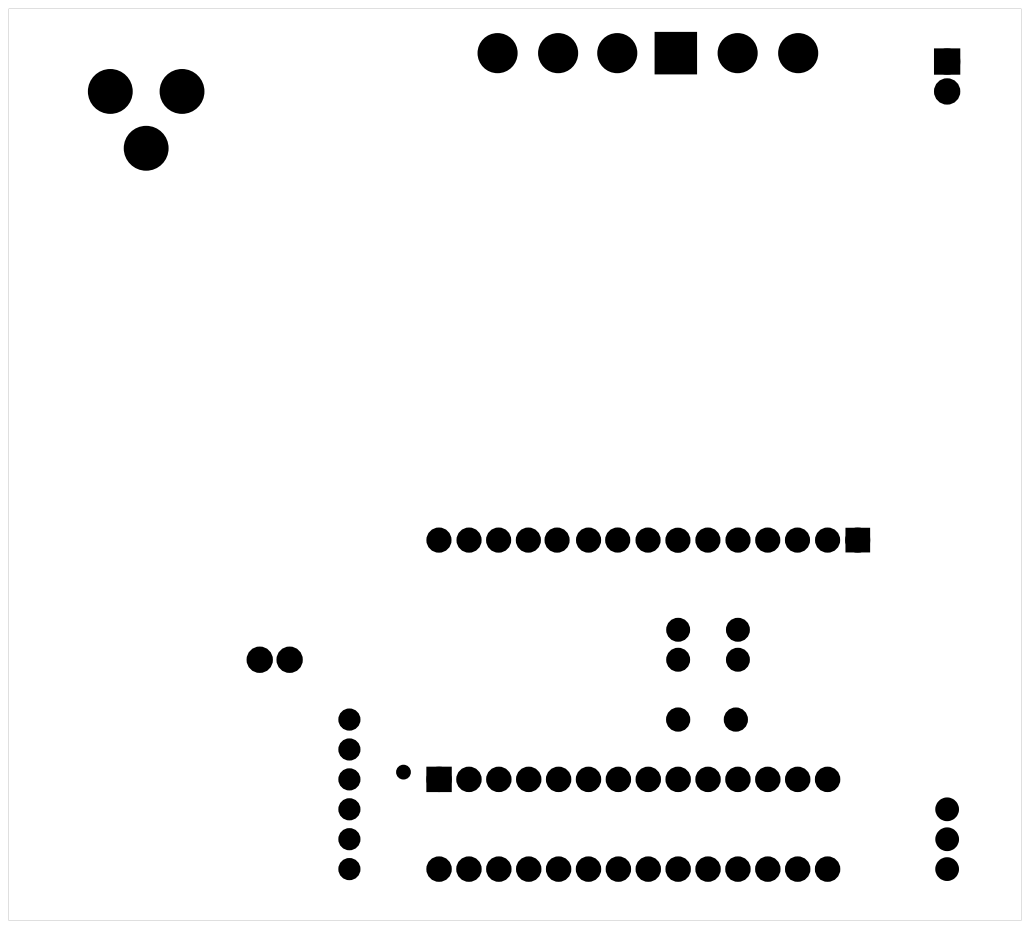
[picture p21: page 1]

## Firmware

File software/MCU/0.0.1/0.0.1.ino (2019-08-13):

/************************************/
/****This code is DEBUG**************/
/***This is not a release version****/
/***Please don't use it in release***/
/************************************/
/*****Juan Blanc****TECSCI 2019******/
/************************************/


#include <Wire.h>
#include <LiquidCrystal_I2C.h>
#include <OneWire.h>
#include <DallasTemperature.h>

byte heat1[8] = {
  0b00101,
  0b00000,
  0b01010,
  0b10000,
  0b00100,
  0b00001,
  0b00100,
  0b10000
};
byte heat2[8] = {
  0b01101,
  0b10000,
  0b00110,
  0b00000,
  0b01001,
  0b10100,
  0b00000,
  0b01010
};
int sensorPin = 1 ;
int currentPin = 0 ;
/* Control part  */

int peltierA = 4 ;  //DIGITAL
int peltierB = 7 ;  //DIGITAL
int enablePeltier = 6 ; //DIGITAL
int pwmPeltier = 5 ;  //DIGITAL


LiquidCrystal_I2C lcd(0x27,16,2);

double kp = 2;
double ki = 5;
double kd = 1;
const int pinDatosDQ = 9;

OneWire oneWire(9);

// declare as sensor referenec by passing oneWire reference to Dallas Temperature.
DallasTemperature sensors(&oneWire);

// declare your device address
// YOUR ADDRESS GOES HERE!!!!
DeviceAddress tempSensor = {0x28, 0xA5, 0x84, 0x01, 0x09, 0x00, 0x00, 0x7C};

// A Variable to hold the temperature you retrieve
float tempC;

void setup(){
  lcd.init();                      // initialize the lcd
  lcd.backlight();
  //sensorDS18B20.begin();
  Serial.begin(9600);

  //sensorDS18B20.setResolution(tempSensor,11);

  //Serial.println(sensorDS18B20.getResolution(tempSensor));
  sensors.setResolution(tempSensor, 12);
  // confirm that we set that resolution by asking the DS18B20 to repeat it back
  /* this was enable in debug mode */
  //Serial.print("Sensor Resolution: ");
  //Serial.println(sensors.getResolution(tempSensor), DEC);
  //Serial.println();

}

void loop(){
  float current = analogRead(currentPin);
  float sensorValue = analogRead(sensorPin);
  sensors.requestTemperaturesByAddress(tempSensor); // Send the command to get temperatures

  // Get the temperature that you told the sensor to measure
  tempC = sensors.getTempC(tempSensor);
  lcd.setCursor(0,0);
  lcd.print(tempC,4);
 String dataToSend = String(tempC,6);
  Serial.println(dataToSend);
  //Serial.println(tempC,6);
  lcd.setCursor(7,0);
  lcd.print("C");
  lcd.setCursor(0,1);

float mVperAmp = 104.7; // use 100 for 20A Module and 66 for 30A Module
                        // change int for float to get more accurate reading

int RawValue= 0;
int ACSoffset = 2500;
float Voltage = 0; //voltage measuring
float Amps = 0;// Current measuring
 RawValue = analogRead(currentPin);//reading the value from the analog pin
 Voltage = (RawValue / 1024.0) * 5000; // Gets you mV
 Amps = ((Voltage - ACSoffset) / mVperAmp) * (-1);
  lcd.print(Amps);
  lcd.setCursor(6,1);
  lcd.print("A");
float  set_temp = 45.00;
 if (tempC < set_temp){

  lcd.setCursor(8,0);
  lcd.print("Heating!");
  lcd.setCursor(8,1);
  lcd.print("Pel.Ext");
  heatPlease(1);
 }
if (tempC > (set_temp + 0.05) && tempC <= (set_temp + 0.10 )){
  heatPlease(0);
  lcd.setCursor(8,0);
  lcd.print("Good!    ");
  lcd.setCursor(8,1);
  lcd.print("Pel.Stop");
}
 if (tempC > (set_temp + 0.10) ){
  lcd.setCursor(8,0);
  lcd.print("Cooling!");
  lcd.setCursor(8,1);
  lcd.print("Pel");
 // coolPlease(1);

  }
  delay(1000);
}




void heatPlease(bool enable)
{
  digitalWrite(peltierA,HIGH);
  digitalWrite(peltierB,LOW);
  if (enable == 1 || enable == true)
  {
    digitalWrite(enablePeltier,HIGH);
    analogWrite(pwmPeltier,255);
  }
  else
  {
    digitalWrite(enablePeltier,LOW);
    analogWrite(pwmPeltier,0);
  }

}
void coolPlease(bool enable)
{
  digitalWrite(peltierA,LOW);
  digitalWrite(peltierB,HIGH);
  if (enable == 1 || enable == true)
  {
    digitalWrite(enablePeltier,HIGH);
    analogWrite(pwmPeltier,255);
  }
  else
  {
    digitalWrite(enablePeltier,LOW);
    analogWrite(pwmPeltier,0);
  }
}

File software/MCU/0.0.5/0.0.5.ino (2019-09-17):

/************************************/
/*****This code is DEBUG*************/
/*****This is not a release version**/
/*****Please don't use it in release*/
/************************************/
/*****Juan Blanc***TECSCI 2019*******/
/************************************/
/**********Version 0.0.5*************/
/************************************/

/*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
    You should have received a copy of the GNU General Public License
    along with this program.  If not, see <https://www.gnu.org/licenses/>. */
#include <Arduino.h>
#include <Adafruit_Sensor.h>
#include <Adafruit_BME280.h>
#include <PID_v1.h>
#include <Wire.h>
#include <OneWire.h>
#include <DallasTemperature.h>
#include <LiquidCrystal_I2C.h>
#include "peltier.h"

//needed for library
#define SEALEVELPRESSURE_HPA (1020)

/* pin to connect the DS18B20 sensor */
const int pinDataDQ = 17;

/* Object creation of Temperature sensor and lcdScreen */
Adafruit_BME280 bme;
peltier thePeltier ;

//TIME FOR DRAW!
byte UsingPID[] = {0x06,0x05,0x06,0x15,0x01,0x13,0x15,0x13};
byte notUsingPID[] = {0x04,0x0E,0x15,0x15,0x04,0x0E,0x1F,0x1F};
byte bigP[] = {0x1E,0x11,0x11,0x1E,0x18,0x18,0x18,0x19};
byte bigH[] = {0x14,0x1C,0x14,0x06,0x09,0x0E,0x08,0x07};
byte steadySign[] = {0x0C,0x10,0x08,0x04,0x18,0x07,0x02,0x02};
byte microActivity[] = {0x0C,0x10,0x10,0x0C,0x02,0x05,0x07,0x05};

//Define Variables we'll be connecting to
double Setpoint, Input, Output;
float temperature_read = 0;

//Pins
int peltierA = 32 ;  //Digital GPIO
int peltierB = 33 ;  //Digital GPIO
int enablePeltier = 25 ; //Digital GPIO
int pwmPeltier = 26 ;    //Used to control the driver GPIO

//Define the aggressive and conservative Tuning Parameters
double aggKp=4, aggKi=.225, aggKd=8;
double consKp=.3, consKi=.15, consKd=.4;


OneWire oneWireObject(pinDataDQ);
DallasTemperature sensorDS18B20(&oneWireObject);

PID myPID(&Input, &Output, &Setpoint, consKp, consKi, consKd, DIRECT);

LiquidCrystal_I2C lcd(0x27,16,2);

/* EXPERIMENTAL  */

int pinA = 2; // InterruptHardware Pin Digital GPIO 2
int pinB = 15; // Interrupt Hardware Pin Digital GPIO 15
volatile byte aFlag = 0; // let's us know when we're expecting a rising edge on pinA to signal that the encoder has arrived at a detent
volatile byte bFlag = 0; // let's us know when we're expecting a rising edge on pinB to signal that the encoder has arrived at a detent (opposite direction to when aFlag is set)
volatile byte reading = 0; //somewhere to store the direct values we read from our interrupt pins before checking to see if we have moved a whole detent

const byte  buttonPin = 8;
byte        oldButtonState = HIGH;  // assume switch open because of pull-up resistor
byte        buttonState;
const unsigned long debounceTime = 10;  // milliseconds
unsigned long buttonPressTime;  // when the switch last changed state
bool buttonPressed = 0; // a flag variable

void setup()
{
thePeltier.createPeltier(peltierA,peltierB,enablePeltier,pwmPeltier);

  //initialize the variables we're linked to
   lcd.init();
    lcd.backlight();
      lcd.createChar(0, bigP);
         lcd.createChar(1, bigH);
          lcd.createChar(2, UsingPID);
           lcd.createChar(3, steadySign);
            lcd.createChar(4, microActivity);
       sensorDS18B20.begin();
     sensorDS18B20.setResolution(12);
  Serial.begin(9600);
  if (!bme.begin(0x76)) {
    lcd.setCursor(0,0);
      lcd.print("ALARM!!");
      lcd.setCursor(0,1);
      lcd.print("B1- No Amb sensor");
      Serial.println("ErrorSensorAmbiente");
      delay(1000);
      lcd.clear();
      delay(1000);
  }
   /*First message lcd and string constants */
  lcd.setCursor(9,0);
  lcd.print("TWB 1.5");
  delay(1500);
  lcd.setCursor(9,0);
  lcd.print("       ");
  lcd.setCursor(0,0);
  lcd.print("Act:");
  lcd.setCursor(0,1);
  lcd.print("Set:");
  lcd.setCursor(10,1);
  lcd.print("P:");
/* end messages and strings constants */

 /* end begins */
  Input = sensorDS18B20.getTempCByIndex(0);
  Setpoint = temperature_read;

/* Safe test, is the sensor plugged in? */
sensorDS18B20.requestTemperatures();
if (sensorDS18B20.getTempCByIndex(0) < (-4))
{
  while (true)
  {
      lcd.setCursor(0,0);
      lcd.print("ALARM!!");
      lcd.setCursor(0,1);
      lcd.print("S1-chk n' reboot");
      Serial.println("SensorDS18B20Error"); 
      delay(1000);
      lcd.clear();
      delay(1000);
  }
}
/* end safe test */

/*turn the PID on*/
  myPID.SetMode(AUTOMATIC);

Setpoint = bme.readTemperature();
  /* END SETUP */
}

void loop()
{
  sensorDS18B20.requestTemperatures();
  lcd.setCursor(4,0);
  lcd.print(sensorDS18B20.getTempCByIndex(0),2);
  lcd.setCursor(4,1);
  lcd.print(Setpoint);
  Input = sensorDS18B20.getTempCByIndex(0);

  double gap = abs(Setpoint-Input); //distance away from setpoint

  if (gap < 10)
  {  //we're close to setpoint, use CONSERVATIVE tuning parameters
    myPID.SetTunings(consKp, consKi, consKd);
    lcd.setCursor(14,0);
    lcd.write(2);
  }
  else
  {
     //we're far from setpoint, use AGGRESIVE tuning parameters
     myPID.SetTunings(aggKp, aggKi, aggKd);
      lcd.setCursor(14,0);
      lcd.write(2);
  }

  myPID.Compute();

  if(Output<30){
  lcd.setCursor(12,1);
  lcd.print(Output);
   lcd.setCursor(15,0);
   lcd.print(" ");
   thePeltier.heat(1, Output);
  }
  else
  {
     lcd.setCursor(14,0);

      lcd.print(" ");
  }

  if(Output = 0 || Output < 2)
  {
  lcd.setCursor(15,0);

  lcd.write(3);  //Stedy sign
  }

/* Monitoring */
Serial.println(sensorDS18B20.getTempCByIndex(0),4);

/* Comp. Activity blink */
lcd.setCursor(15,1);
lcd.write(4);

}

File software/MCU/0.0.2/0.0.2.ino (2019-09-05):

/************************************/
/*****This code is DEBUG*************/
/*****This is not a release version**/
/*****Please don't use it in release*/
/************************************/
/*****Juan Blanc***TECSCI 2019*******/
/************************************/
/**********Version 0.0.2*************/
/************************************/

/*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
    You should have received a copy of the GNU General Public License
    along with this program.  If not, see <https://www.gnu.org/licenses/>. */

#include <Wire.h>
#include <LiquidCrystal_I2C.h>
#include <OneWire.h>
#include <DallasTemperature.h>

//TIME FOR DRAW!
byte UsingPID[] = {0x00,0x00,0x00,0x00,0x04,0x0E,0x1F,0x1F};
byte notUsingPID[] = {0x04,0x0E,0x15,0x15,0x04,0x0E,0x1F,0x1F};
byte bigP[] = {0x1E,0x11,0x11,0x1E,0x18,0x18,0x18,0x19};
byte bigH[] = {0x14,0x1C,0x14,0x06,0x09,0x0E,0x08,0x07};
byte steadySign[] = {0x0C,0x10,0x08,0x04,0x18,0x07,0x02,0x02};
byte microActivity[] = {0x0C,0x10,0x10,0x0C,0x02,0x05,0x07,0x05};

//Pins
int peltierA = 4 ;  //Digital
int peltierB = 7 ;  //Digital
int enablePeltier = 6 ; //Digital
int pwmPeltier = 5 ;    //Used to control the driver

//Variables
float temperature_read = 0.0;

//IMPORTANT
float set_temperature = 55.5;
//END IMPORTANT

/* For PID Control */
float PID_error = 0;
float previous_error = 0;
float elapsedTime, Time, timePrev;
int PID_value = 0;
int currentPin = 0 ;

// This is for testing
float porcentage = (set_temperature*96.989)/100; //to 98% of power

//PD constants
int kp = 430 ;  int kd = 100;
int PID_p = 0;   int PID_d = 0;

/* pin to connect the DS18B20 sensor */
const int pinDataDQ = 9;

/* Object creation of Temperature sensor and lcdScreen */

OneWire oneWireObject(pinDataDQ);
DallasTemperature sensorDS18B20(&oneWireObject);
LiquidCrystal_I2C lcd(0x27,16,2);

/* Setup */
void setup() {
  /* All the requierd begins and custom character creations */
  lcd.init();
    lcd.backlight();
      lcd.createChar(0, bigP);
         lcd.createChar(1, bigH);
          lcd.createChar(2, UsingPID);
           lcd.createChar(3, steadySign);
            lcd.createChar(4, microActivity);
      sensorDS18B20.begin();
     sensorDS18B20.setResolution(12);
  Serial.begin(9600);
 /* end begins */

 /*First message lcd and string constants */
  lcd.setCursor(9,0);
  lcd.print("TWB 1.2");
  delay(1500);
  lcd.setCursor(9,0);
  lcd.print("       ");
  lcd.setCursor(0,0);
  lcd.print("Act:");
  lcd.setCursor(0,1);
  lcd.print("Set:");
  lcd.setCursor(10,1);
  lcd.print("R:");
/* end messages and strings constants */

/* Safe test, is the sensor plugged in? */
sensorDS18B20.requestTemperatures();
if (sensorDS18B20.getTempCByIndex(0) < (-4))
{
  while (true)
  {
      lcd.setCursor(0,0);
      lcd.print("ALARM!!");
      lcd.setCursor(0,1);
      lcd.print("S1-chk n' reboot");
      delay(1000);
      lcd.clear();
      delay(1000);
  }
}
/* end safe test */
}

/*  main loop */
void loop() {
  sensorDS18B20.requestTemperatures();
  lcd.setCursor(4,0);
  lcd.print(sensorDS18B20.getTempCByIndex(0),2);
  lcd.setCursor(4,1);
  lcd.print(set_temperature,2);

  delay(1000);

/* This part is designed to reach the maximum speed, while approching to the end */
  if (porcentage > sensorDS18B20.getTempCByIndex(0))  //Max poweer
  {
    //please heat/cool to max power
 if (sensorDS18B20.getTempCByIndex(0) < set_temperature){
  heatPlease(1,255);
  lcd.setCursor(14,0);
  lcd.write(1);
  lcd.setCursor(12,1);
  lcd.print("Mx");
 }
}
  else    //please use P-D Control
  {
  /* now we request the temperatures to the DS18B20 */
  sensorDS18B20.requestTemperatures();
  temperature_read = sensorDS18B20.getTempCByIndex(0);
  /*Next we calculate the error between the setpoint and the real value*/
  PID_error = set_temperature - temperature_read;
  /*Calculate the P value*/
  PID_p = kp * PID_error;

  /*For derivative we need real time to calculate speed change rate*/
  timePrev = Time;                            // the previous time is stored before the actual time read
  Time = millis();                            // actual time read
  elapsedTime = (Time - timePrev) / 1000;
  /*Now we can calculate the D calue */
  PID_d = kd*((PID_error - previous_error)/elapsedTime);
  /*Final total PID value is the sum of P + I + D */
  PID_value = PID_p + PID_d; //PID_i is zero

  //We define PWM range between 0 and 255
  if(PID_value < 0)
  {    PID_value = 0;    }
  if(PID_value > 255)
  {    PID_value = 255;  }
  //Now we can write the PWM signal to the driver

  previous_error = PID_error;     //Remember to store the previous error for next loop.
  lcd.setCursor(15,1);
  lcd.print(" ");
  lcd.setCursor(4,0);
  lcd.print(sensorDS18B20.getTempCByIndex(0),2);
  lcd.setCursor(4,1);
  lcd.print(set_temperature,1);
   if (100> PID_value){
    lcd.setCursor(15,1);
    lcd.print(" ");
    }

   lcd.setCursor(12,1);
  lcd.print(PID_value);

 if (sensorDS18B20.getTempCByIndex(0) < set_temperature){

  heatPlease(1,PID_value);  /*Now jump to the function */
  lcd.setCursor(14,0);
  lcd.write(1);
 }
if (sensorDS18B20.getTempCByIndex(0) == (set_temperature) && sensorDS18B20.getTempCByIndex(0) <= (set_temperature + 0.15) )
{
  lcd.setCursor(14,0);
  lcd.write(3);
  heatPlease(1,PID_value); //to maintain the temperature
}
  }  /* end of P-D Control */

/* Comp. Activity blink */
lcd.setCursor(15,1);
lcd.write(4);

/* Monitoring */
Serial.println(sensorDS18B20.getTempCByIndex(0),4);
delay(350);
   if (100> PID_value){
    lcd.setCursor(14,1);
    lcd.print(" ");
    }
}
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

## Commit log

2019-08-16 added version 0.0.2 of the arduino code
2019-08-22 Design 0.1 schematics
    [DesignVer0.1.fzz]
2019-08-22 Tools for testing Peltier with driver
    [main.fzz]
2019-08-22 new file with corrections of errors
    [DesignVer0.1.fzz]
2019-08-26 gerber file
    [DesignVer0.1_contour.gm1, DesignVer0.1_copperBottom.gbl, DesignVer0.1_copperTop.gtl, DesignVer0.1_maskBottom.gbs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]
2019-08-26 BOM file
    [Electronic_BOM.csv]
2019-08-27 New BOM
    [Electronic_BOM.csv]
2019-08-29 Stl files uploaded & frame.md modification
    [ThermostaticWaterBathv2.stl]
2019-10-25 new version of the code, new libraries and framework

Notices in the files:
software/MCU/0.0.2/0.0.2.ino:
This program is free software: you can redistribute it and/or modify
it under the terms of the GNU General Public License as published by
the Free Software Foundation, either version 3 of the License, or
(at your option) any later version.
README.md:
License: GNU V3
